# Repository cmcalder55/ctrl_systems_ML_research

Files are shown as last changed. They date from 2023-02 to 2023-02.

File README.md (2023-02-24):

# &nbsp;&nbsp;&nbsp;&nbsp;&nbsp;&nbsp;&nbsp;&nbsp;&nbsp;&nbsp;&nbsp;&nbsp;&nbsp;&nbsp;&nbsp;&nbsp;&nbsp;&nbsp;&nbsp;Automation and Machine Learning for Robust   &nbsp;&nbsp;&nbsp;&nbsp;&nbsp;&nbsp;&nbsp;&nbsp;&nbsp;&nbsp;&nbsp;&nbsp;&nbsp;&nbsp;&nbsp;&nbsp;&nbsp;&nbsp;&nbsp;&nbsp;&nbsp;&nbsp;&nbsp;&nbsp;&nbsp;&nbsp;Self-Tuning of Magneto-Optical Traps

## Abstract  
In recent years the Magneto-Optical Trap (MOT) has become a standard technology used in almost every AMO laboratory (Atomic, Molecular, and Optical Physics). While technology of individual components has improved over time, the alignment of the trap still requires tedious maintenance performed hands-on by skilled experimentalists. The project focuses on developing a custom control system for piezoelectric mirror mounts responsible for the position adjustment of the lasers beams in the experimental setup. The implementation consists of LabVIEW interface and python algorithms, supported by rotary encoders to correct for hysteresis of the devices. The control system’s efficiency is tested through fiber coupling, typically performed manually, with the overall goal of full automation. This contributes to the group’s goal of automating the MOT as a whole, thereby saving time and making experimental results more repeatable. 

The feedback from the LabVIEW controllers is used in the Python program to determine the position of the center of the fiber cable and aim the laser. After successful coupling, machine learning models are used to evaluate the outputs of the entire experiment and determine the optimal experimental inputs. These models also help reveal any correlations between the mirror position, laser and fiber coupling, the rate of successful cloud creation, and the characterisitics of any resulting atom clouds. By implementing these controllers and evaluation systems, the overall goal is to fully automate this process and the experiment as a whole.

<p align="center">
Atom cloud experimental output

<p align = "center">
Fig.1 - MOT atom cloud.
</p>

## Introduction  
Magneto-optical traps (MOTs) use lasers and magnetic fields to cool and slow down atoms. Atoms are cooled down to temperatures as low as ~15 uK, which is almost absolute zero. Atoms are fed into the experiment where they collide with lasers on the x,y, and z axes. The photons in the laser collide with the atoms and cancel out some of their momentum and push them towards the laser source. This causes friction on the atoms, slowing them further with the Doppler cooling effect. Magnetic fields in a vaccuum chamber are used to pull cooled atoms towards the center and create a "trap". Atoms in the experiment are run through the phases of this trap system multiple times, with the goal of creating a cloud of atoms that is as dense and as cold as possible.

<p align="center">

&nbsp;&nbsp;&nbsp;&nbsp;&nbsp;&nbsp;&nbsp;&nbsp;&nbsp;&nbsp;&nbsp;&nbsp;

</p>

<p align = "left">
&nbsp;&nbsp;&nbsp;&nbsp;&nbsp;&nbsp;&nbsp;&nbsp;&nbsp;&nbsp;&nbsp;&nbsp;&nbsp;&nbsp;&nbsp;&nbsp;&nbsp;&nbsp;&nbsp;&nbsp;&nbsp;&nbsp;&nbsp;&nbsp;&nbsp;&nbsp;&nbsp;&nbsp;&nbsp;&nbsp;&nbsp;&nbsp;&nbsp;&nbsp;&nbsp;&nbsp;&nbsp;Fig.2 - Slowing of atoms with photons.&nbsp;&nbsp;&nbsp;&nbsp;&nbsp;&nbsp;&nbsp;&nbsp;&nbsp;&nbsp;&nbsp;&nbsp;&nbsp;&nbsp;&nbsp;&nbsp;&nbsp;&nbsp;&nbsp;&nbsp;&nbsp;&nbsp;Fig.3 - MOT basic experimental setup.
</p>
  
Slowing down the atoms makes it significantly easier to study the atom's quantum characteristics. For example, if you are trying to read the license plate on a car, the slower the car the easier it is to read. The same concept applies to quantum properties of atoms. There are many parameters that must be controlled to run this experiment, typically requiring multiple skilled experimentalists and a huge time investment just to set up. It is very sensitive to environmental variables like ambient temperature and light, making it difficult to maintain experimental conditions. Very small changes such as microscropic drift over time in parts of the experimental setup can be the difference between a successful run and no atom cloud output at all.  

## Motivation
The overall objective of this project was to use automation approaches and optimization and machine learning techniques to remove the need for a trained operator to tune the MOT. Tuning by a human operator is extremely time consuming, and can take anywhere from six hours to days, with no guarantee of a successful experimental output. The experimental set-up is also very crowded and difficult to adjust by hand, and uses high-powered lasers that pose a safety risk while making hand adjustments. By automating these mirror mount adjustments and making them remotely controllable, the experiment will become easier to repeat and safer for experimentalists to run. Significantly reducing the set-up time also allows more runs to be done in the same time frame, allowing the group to identify the factors needed to consistently generate an atom cloud.   
  
**The individual goals were to:**  
  * Find appropriate transducers to get the relative position of the mirror mount adjusters  
  * Design and build a mechanism to attach the transducers to the mounts  
  * Make a LabVIEW program to:  
    * Remotely control the mount adjusters   
    * Determine their absolute position using the transducers  
  * Make the control system closed loop to compensate for hysteresis  
  * Write a Python program to run the LabVIEW program and optimize mirror adjustments  
  * Use machine learning libraries in Python to analyze experimental outputs and explore coupling profiles  

### Commercial Solutions
A huge limitation to solving this problem to automatic mount adjustment is the high level of precision required and lack of space in the set-up to add transducers. When working on an atomic level, an adjustment of a few micrometers can completely misalign a mirror. Stepper motors, for example, can be controlled remotely and make fine adjustments, but they are too large and unstable to use.   
The mirror mounts on the experiment also function using a piezoelectric material, so they have a high hysteresis rate and have no built-in compensation system. Inertial actuators can be added to help have a more consistent step-size during adjustment, but they still have an open-loop design with up to 20% error between steps. The inertial actuators also limit the range of the adjuster screws while doubling their profile length, making them unusable.

<p align="center">

&nbsp;&nbsp;&nbsp;&nbsp;&nbsp;&nbsp;&nbsp;&nbsp;&nbsp;

<p align = "center">
Fig.4 - Stepper motor actuators. &nbsp;&nbsp;&nbsp;&nbsp;&nbsp;&nbsp;&nbsp;&nbsp;&nbsp;&nbsp;&nbsp;&nbsp;&nbsp;&nbsp;&nbsp;&nbsp;&nbsp;&nbsp;Fig.5 - Inertial actuators.
</p>

### Repeatability Trade-Off
The piezoelectric mirror mounts come with a controller that can be operated remotely, but the controls are not customizable to the level needed for this experiment, and the screw distance travelled is not repeatable. However, it is possible to make very fine adjustments manually due to the piezoelectric effect. This also has the advantage of being self-locking while at rest or while no power is applied, but the adjustments made to get to a position are not repeatable. This is due to a variety of reasons such as variation between mount components, variable friction when turning the screw forwards or backwards, and high hysteresis when making steps of the same size. 

<p align="center">

<p align = "center">
Fig.5 - Example of difference between forward and reverse step sizes of same input magnitude.
</p>

## Methods  
[Detailed descriptions of every component in the system and their function can be found **HERE**.](https://github.com/cmcalder55/ctrl_systems_ML_research/blob/main/LV_code_and_guide/Mount_Control_VI_Guide_2.pdf)

To compensate for this error, small rotary encoders were inserted into the adjuster screws and attached to the mount using existing screw holes. The 360 degree turn of the screw is proportional to the 0-5 V. output of the rotary encoder, giving the relative position of the screw. This information can then be used to create a feedback system using a custom P.I. controller to automatically correct positional error, as well as define and map the global screw position to utilize the full range of adjustments.   

This design is better than the commerical alternatives because the transducers have a small profile and highly accurate. The wiring system is simple (power, groud, output) and outputs an analog voltage signal, making it easy to read into LabVIEW and make an effective automated controller. This solution is also not exclusive to the mounts used in this experiment, and could be added to a wide range of products that have high hysteresis.  

Position commands are input into Python, which are then fed into LabVIEW using a TCP connection. The LabVIEW controller communicates with the native mount controller to move the screws and scale the step size to reach the desired point. A homing mode was also added to set the global origin of the adjuster screws and define the full range of the screw. The absolute position is stored to an external file, so it does not need to be re-callibrated. This is important because the controller still tries to move the screw even if it cannot be turned anymore. This can cause damage to the equipment, so it is necessary to know when a screw is approaching the end of its range. The homing system is summarized in Fig. 6 below.  

<p align="center">

<p align = "center">
Fig.6 - Homing mode control system diagram.
</p>

To move the mirrors the following steps are taken:  
* User inputs desired position
* Average transducer voltage is converted to degrees
* PI controller scales n steps based on direction (P) and degree difference (I)
* Adjuster screw is moved 20% of n steps and degree error is checked
* Continues until error is within desired range of user input
  * If within range, set steps needed to 0

<p align="center">

<p align = "center">
Fig.7 - Move mode P.I. controller feedback system diagram.
</p>

The overall system setup is shown in Fig. 8 below. Detailed descriptions of every component in the system can be found **HERE**. The steps taken can be summarized as follows:  
**1. Top level TCP communication: The “TCP_connection” VI is used to send position data from Python file “TCP_bare” to the mount 
controls subVI. The subVI outputs laser coupling percentage and the value is sent back to Python.**  
  * Read data from Python
  * Send data to subVI
  * Return data from subVI and exit
**2. Mount control subVI: The “mount_controls.vi” subVI receives an array of positions and mode number as inputs. Outputs laser 
coupling percentage.**  
  * Initialize message queue and scan for controller device, return array of controller channels
  * Create array of analog input channels and voltage sampling task
  * Separate channel for reading photodiode to check coupling percentage
  * Cluster mount channels and pairs
  * Determine mode input
    * 1 or 2 = "RUN"
    * 3 = "HOME"
    * 0/default = "END"
 **3. Execute current active mode based on dequeued message**
  * Run --> Read current laser coupling --> queue Move message
  * Move --> make adjustment --> check actual position --> re-adjust until within margin of error --> End
  * End --> store position data --> close queues --> output absolute position  
 
 The photodiode is continuously read during this process to check for any laser coupling by averaging every 100 samples.  
 
 **4. (Optional) Home: home channels and reset stored origin.**
  * Take a step in the reverse direction
  * Keep taking steps and scale by the rate of positional change
  * When the rate of change is sufficiently small, take very small and quick steps
  * Keep taking very small steps until the sensor is no longer moving (end of range of motion)
  * Store home position

<p align="center">

<p align = "center">
Fig.8 - Full system diagram.
</p>

## Results  
Using this custom controller, a user chosen position was repeatable with a high level of accuracy. It was determined that on average, the screw adjustments were 3 times as fast in the forward direction. This indicates that the friction used to move the screws using voltage control with the piezoelectric material had a significant effect on the step size. This effect means that adding a feedback system is the minimum needed to use these mounts with any degree of repeatability.  
  
Another advantage of the system created in this project is an adjustable error margin, allowing for extremely precise movements. After achieving this, the program was used to automate laser coupling with a fiber optic cable. The Python inputs were then switched from user control to inputs chosen by an optimizer made in Python. This was a goos test of accuracy, since this set-up is more sensitive than the MOT itself. After coupling was achieved, a machine learning model was used to discern the effect of coupling on the output of the MOT.

<p align="center">

&nbsp;&nbsp;&nbsp;&nbsp;&nbsp;&nbsp;&nbsp;&nbsp;&nbsp;&nbsp;&nbsp;&nbsp;&nbsp;&nbsp;&nbsp;&nbsp;&nbsp;&nbsp;

<p align = "center">
Fig.9 - Laser coupling testing and automated adjustment system diagram. &nbsp;&nbsp;&nbsp;&nbsp;&nbsp;&nbsp;&nbsp;&nbsp;&nbsp;&nbsp;&nbsp;&nbsp;&nbsp;&nbsp;&nbsp;&nbsp;&nbsp;&nbsp;&nbsp;&nbsp;&nbsp;&nbsp;&nbsp;Fig.10 - Laser coupling experimental setup.
</p>

## Discussion
Dur to time constraints, the machine learning model was not able to make any significant conclusions from the data. However, achieving automated coupling at any level was a significant step towards automating the MOT and reducing set-up time while prioritizing worker safety. If this project were to be continued, the next steps would focus on training the M.L. model with more data and fine-tuning the automated laser coupling set-up on the actual experiment.

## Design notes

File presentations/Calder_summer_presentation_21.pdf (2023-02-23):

## Automation and Machine Learning for Robust

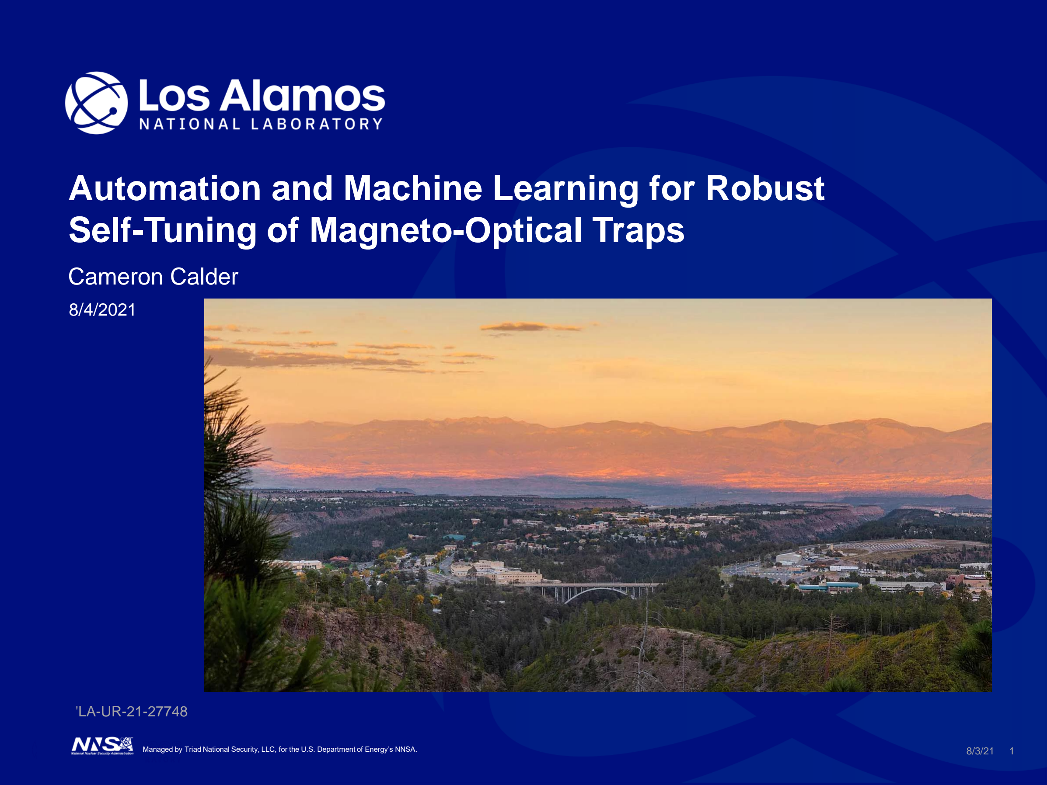
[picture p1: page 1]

Managed by Triad National Security, LLC, for the U.S. Department of Energy’s NNSA. | 8/3/21 | 1

## Self-Tuning of Magneto-Optical Traps

Cameron Calder

8/4/2021

'LA-UR-21-27748

## Motivation

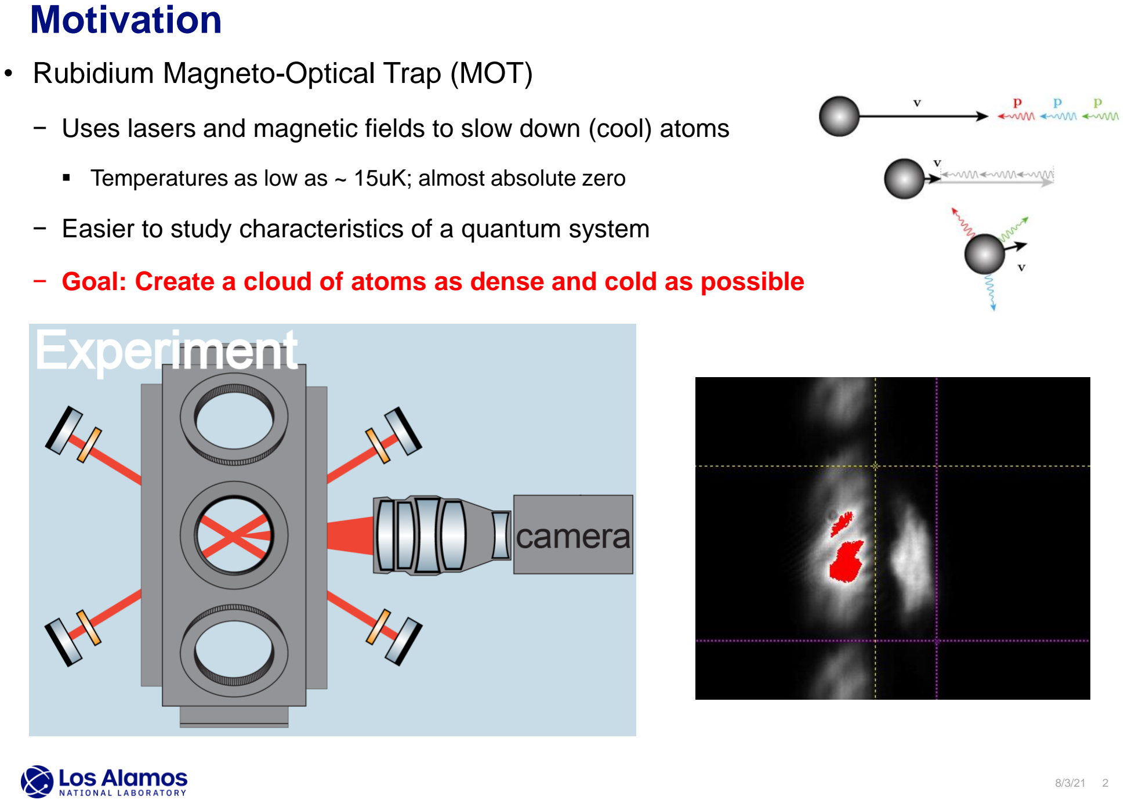
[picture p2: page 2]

8/3/21 2

- Rubidium Magneto-Optical Trap (MOT)

− Uses lasers and magnetic fields to slow down (cool) atoms

- Temperatures as low as ~ 15uK; almost absolute zero

− Easier to study characteristics of a quantum system

− Goal: Create a cloud of atoms as dense and cold as possible

## Experimental Set-Up

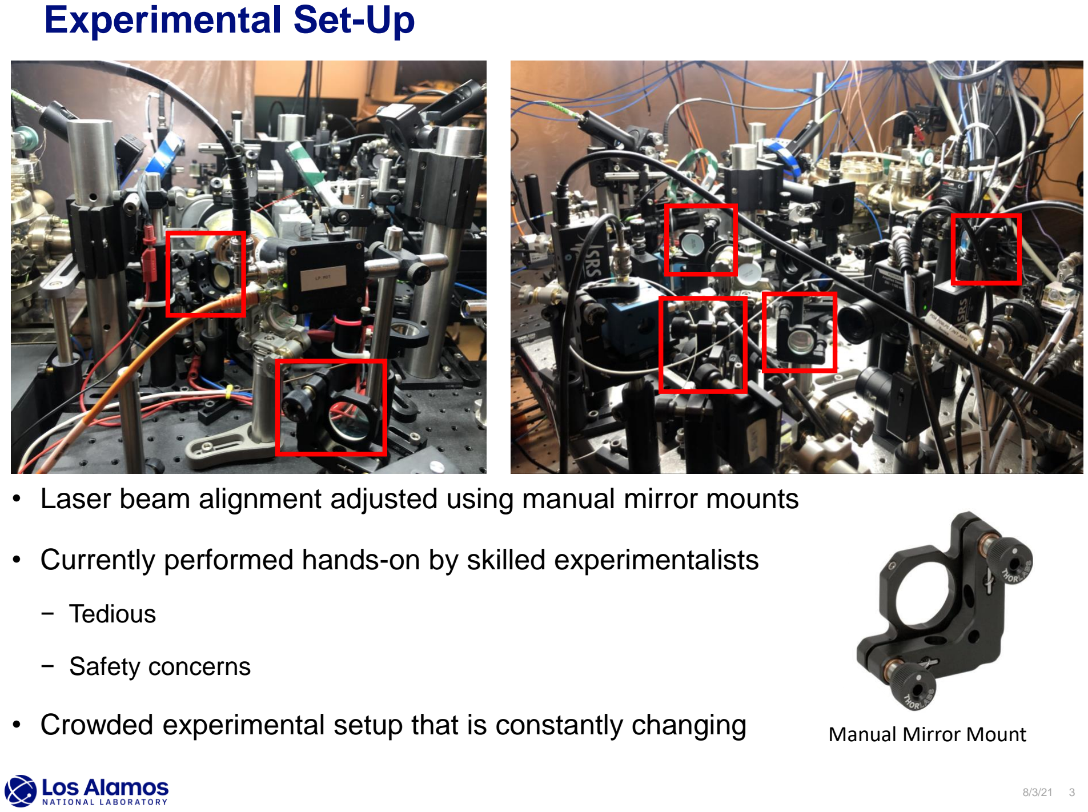
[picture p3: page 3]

- Laser beam alignment adjusted using manual mirror mounts
- Currently performed hands-on by skilled experimentalists

− Tedious

− Safety concerns

- Crowded experimental setup that is constantly changing | Manual Mirror Mount

## Commercial Solutions and Limitations

- Current mounts allow fine adjustment, but can only be moved manually

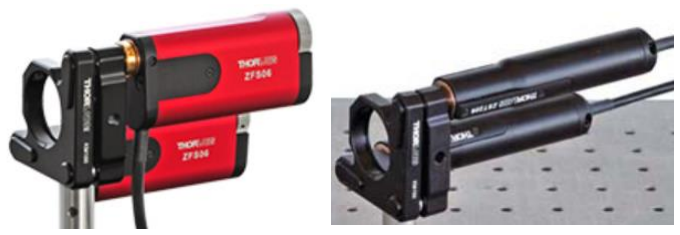
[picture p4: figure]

4:1 Length | 5:1 Length

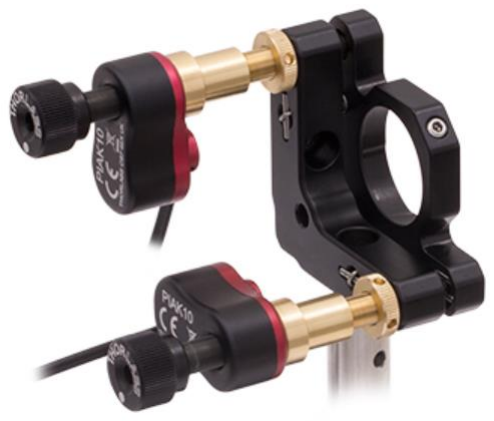
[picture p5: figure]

2:1 Length

- Piezoelectric Inertial Actuator ‒ Cannot move full screw range ‒ Still requires external feedback
- Stepper Motors
‒ Too large
‒ Unstable

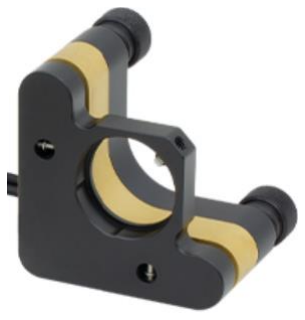
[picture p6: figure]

Piezoelectric Mirror Mount

Manufacturer Solutions

- Piezoelectric mounts can be moved remotely, but screw
distance traveled not repeatable − Fine adjustment
− Similar size

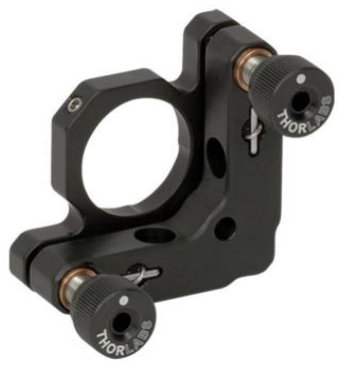
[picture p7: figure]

Manual Mirror Mount

## What is a Piezoelectric Mount?

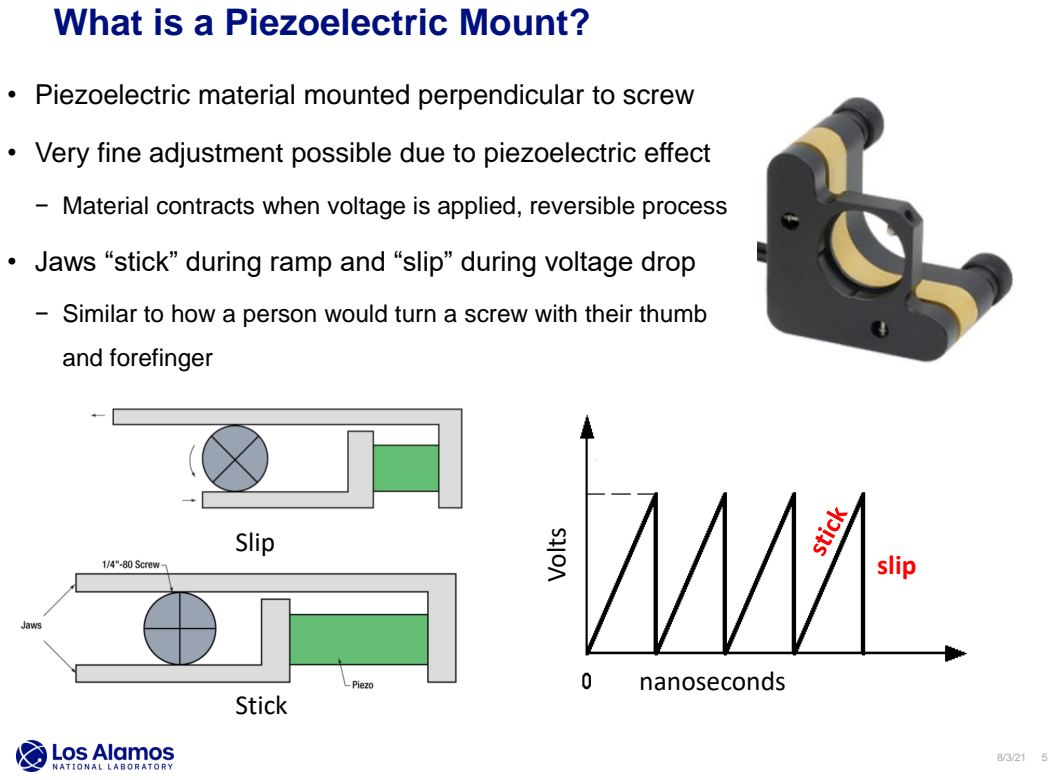
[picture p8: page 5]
and forefinger; slip; nanoseconds; Volts; Slip; Stick

• Piezoelectric material mounted perpendicular to screw

• Very fine adjustment possible due to piezoelectric effect

− Material contracts when voltage is applied, reversible process

• Jaws “stick” during ramp and “slip” during voltage drop

− Similar to how a person would turn a screw with their thumb

## Repeatability Trade-Off

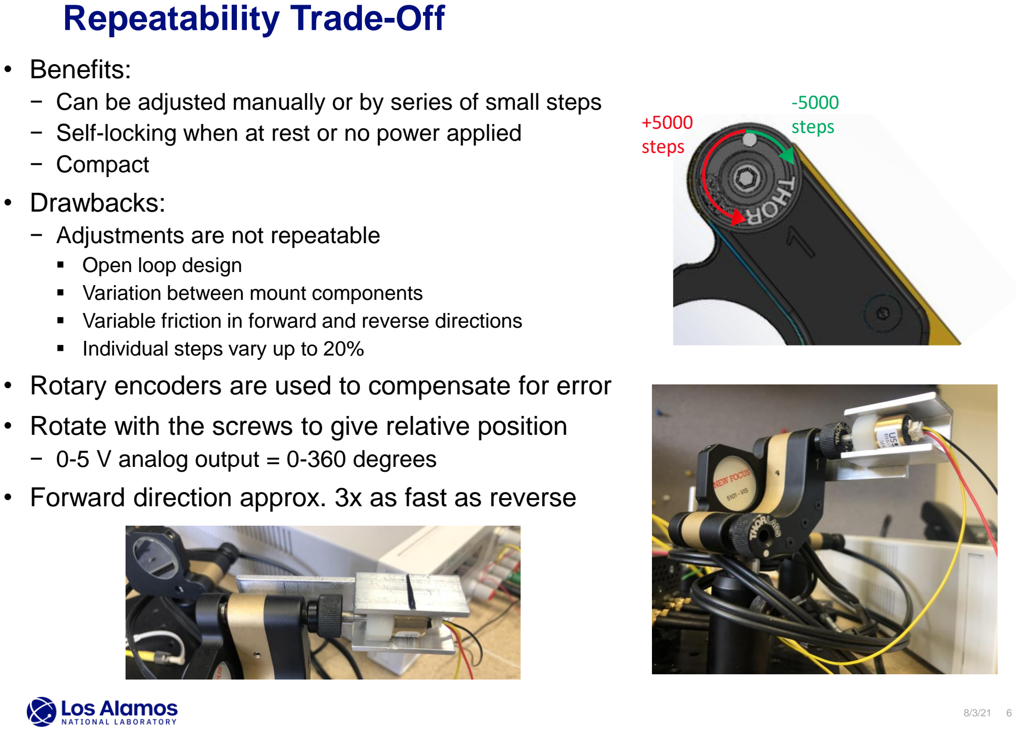
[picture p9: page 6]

+5000
steps

-5000
steps
- Benefits:
− Can be adjusted manually or by series of small steps − Self-locking when at rest or no power applied
− Compact
- Drawbacks:
− Adjustments are not repeatable
- Open loop design
- Variation between mount components
- Variable friction in forward and reverse directions
- Individual steps vary up to 20%
- Rotary encoders are used to compensate for error
- Rotate with the screws to give relative position
− 0-5 V analog output = 0-360 degrees
- Forward direction approx. 3x as fast as reverse

## Why Our Design is Better

- Transducers are small and accurate − 1 step = 0.02 degrees
− 70% the length of the mount
- Easy wiring and analog output
− 3 wires- power, ground, output
− Read using DAQ directly into LabVIEW
- Simple to attach and reproduce
− One Al bracket (1)
− One Al U-channel (2)
− One nylon hex nut (3)
− One plastic spacer (4)
− Two flathead screws (5)
− One mounting screw (6)
- Comparable price
− Solution not exclusive to these mounts

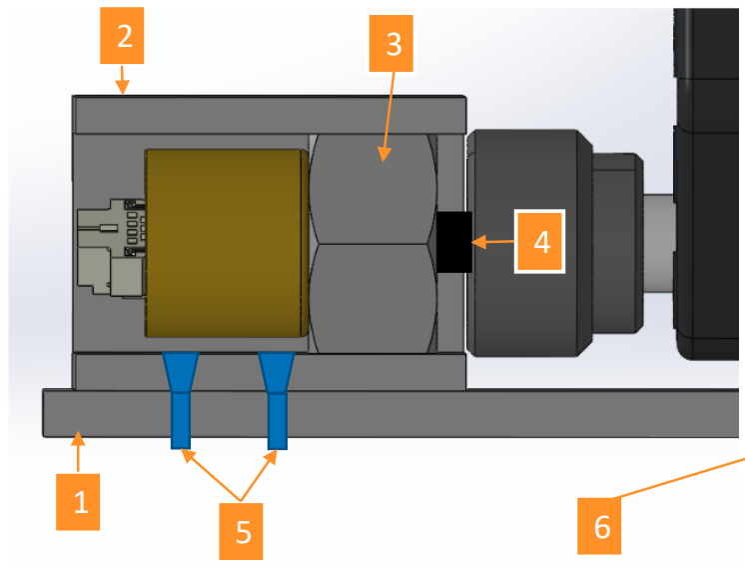
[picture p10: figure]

Solution | Parts Cost ($) | Mount Cost ($) | Total Cost ($)
Rotary Encoder | 130 | 1200 | 1330
Stepper Motor 1 | 2200 | 40 | 2240
Stepper Motor 2 | 1300 | 40 | 1340

## Overall Adjuster Screw Control System

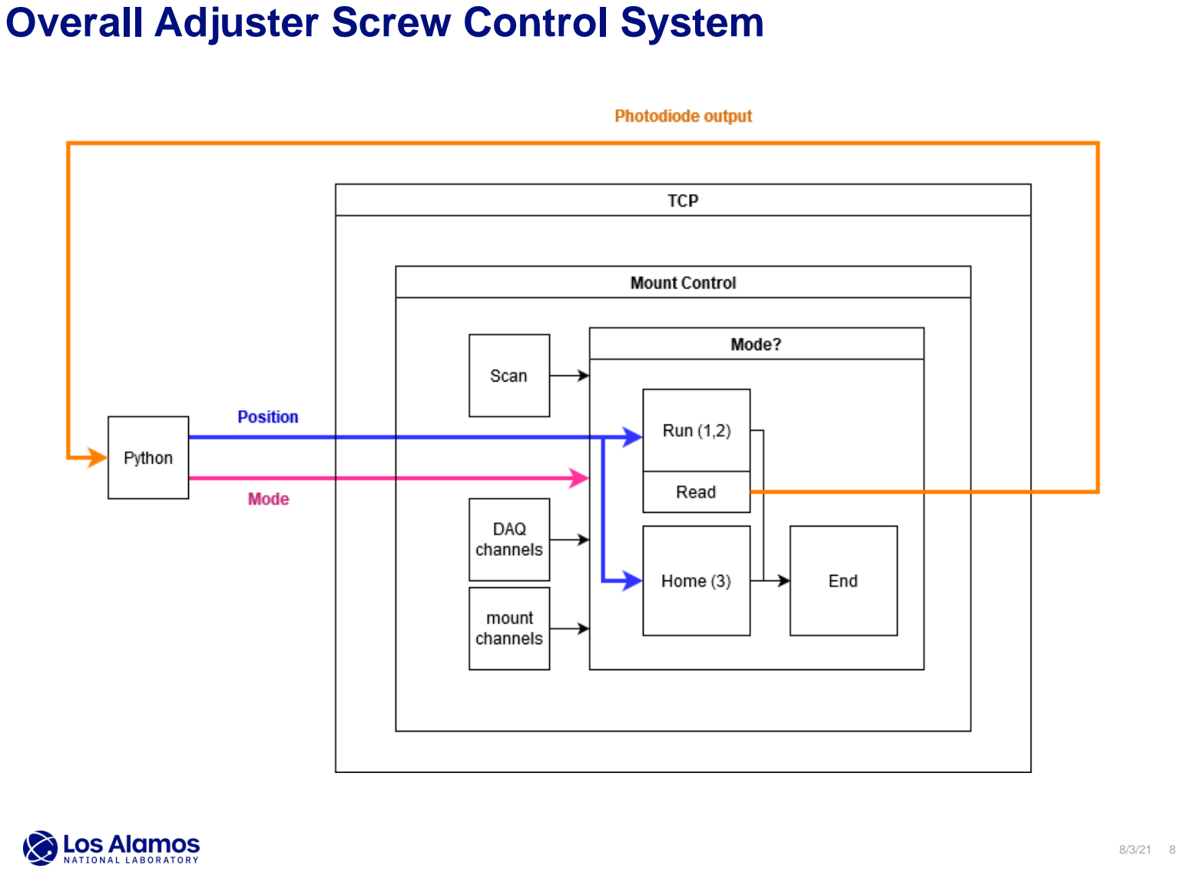
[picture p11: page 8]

## Finding Home

- Transducer only has range of 0-360 degrees
− One rotation
- Overall screw range is 12.7 full rotations
- How can we control the screw over the entire range?

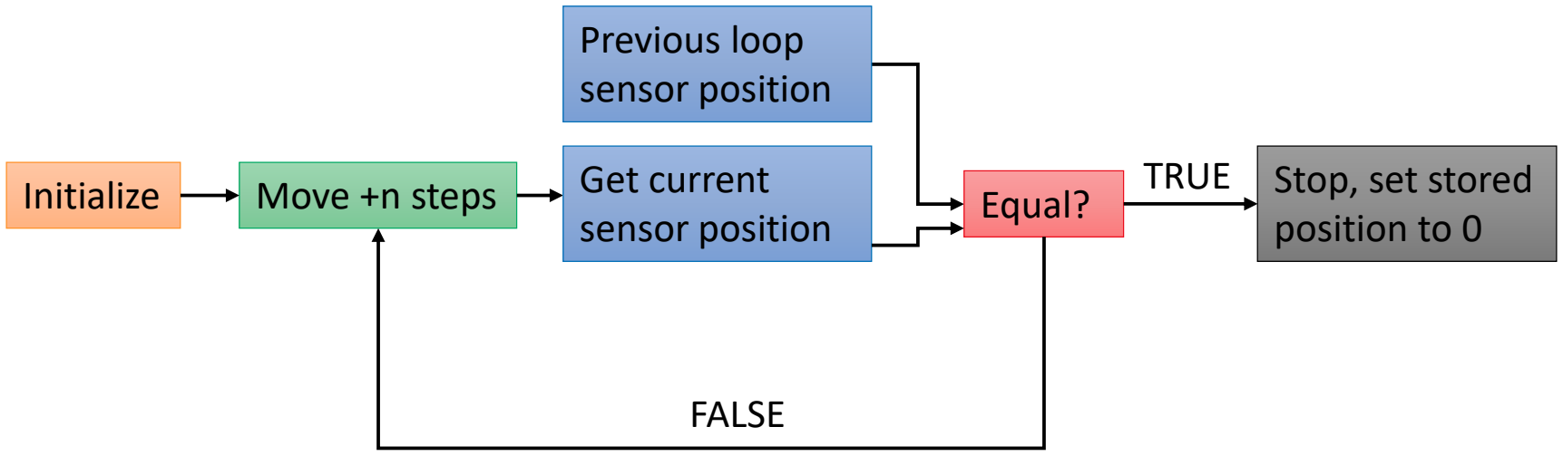
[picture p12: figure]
Initialize; Move +n steps; Get current; sensor position; Previous loop sensor position; FALSE; Equal?; Stop, set stored; position to 0; TRUE

- Only have to initialize on first run
- Absolute position stored to file after screw adjustment based on step change from 0
- Step position / 360 = rotation position

## Using Feedback for Accurate Adjustment

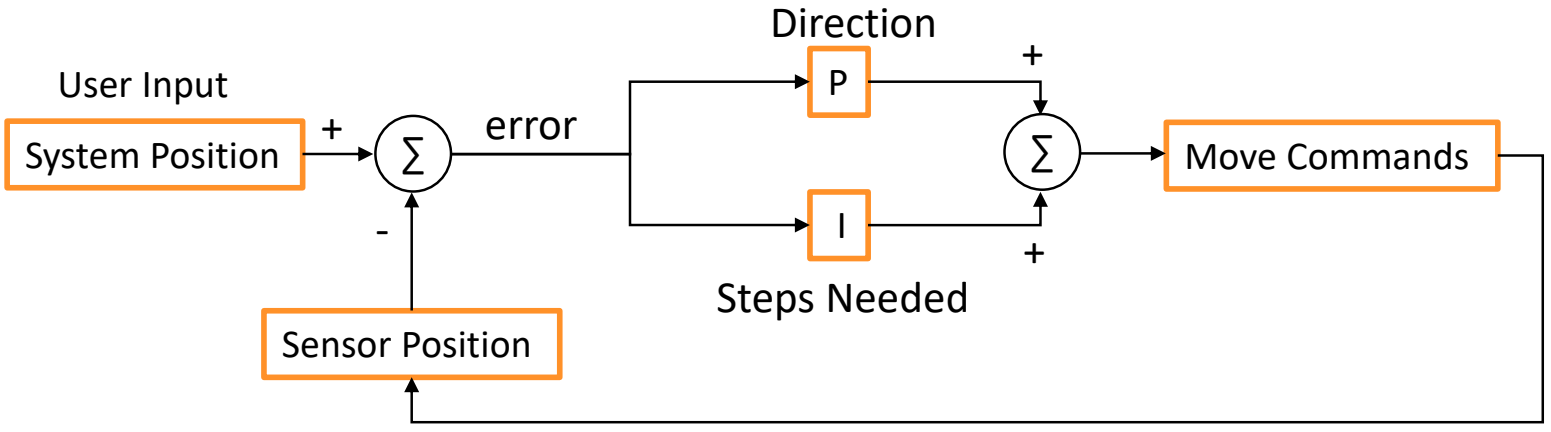
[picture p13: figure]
Sensor Position; System Position; User Input; Move Commands; error; Direction; Steps Needed

- User inputs desired position
- Average transducer voltage is converted to degrees
- PI controller scales n steps based on direction (P) and degree difference (I)
- Adjuster screw is moved 20% of n steps and degree error is checked
- Continues until error is within desired range of user input
− If within range, set steps needed to 0

## System Response

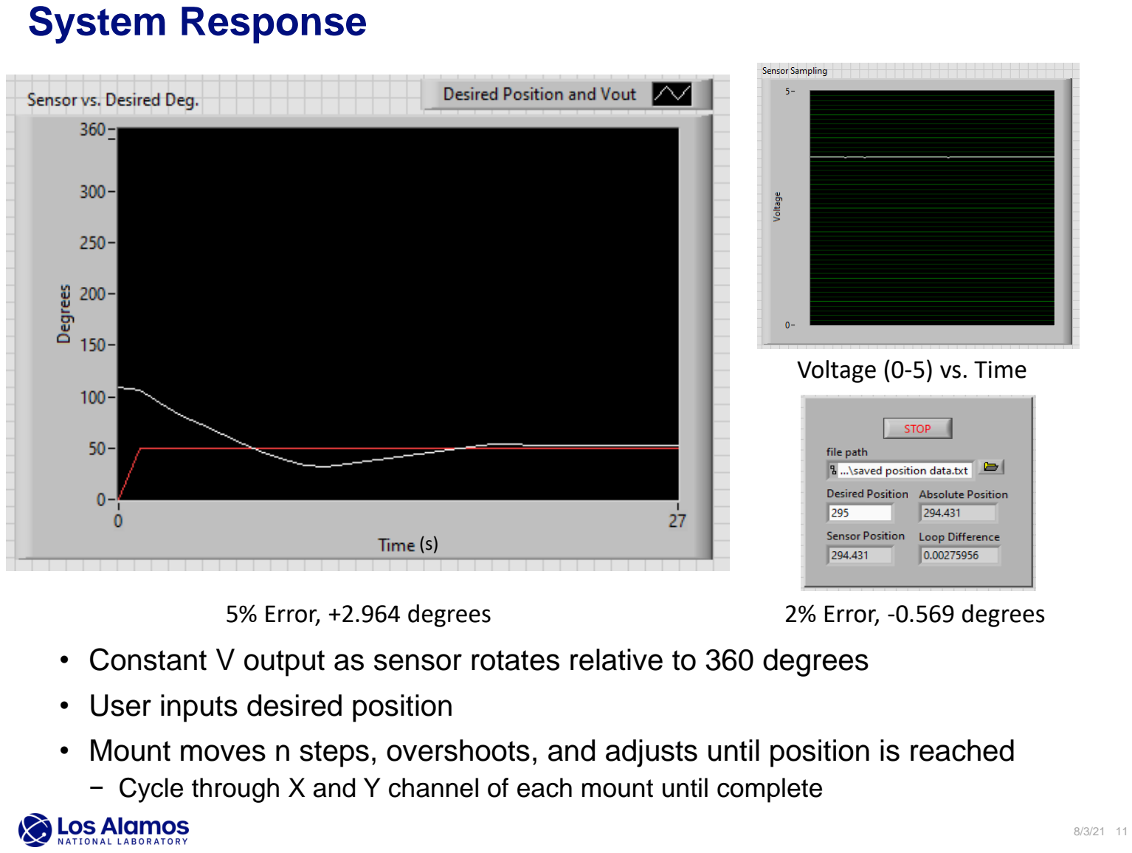
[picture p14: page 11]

- Constant V output as sensor rotates relative to 360 degrees
- User inputs desired position
- Mount moves n steps, overshoots, and adjusts until position is reached − Cycle through X and Y channel of each mount until complete
5% Error, +2.964 degrees | 2% Error, -0.569 degrees
(s) | Voltage (0-5) vs. Time

## Testing and Optimization

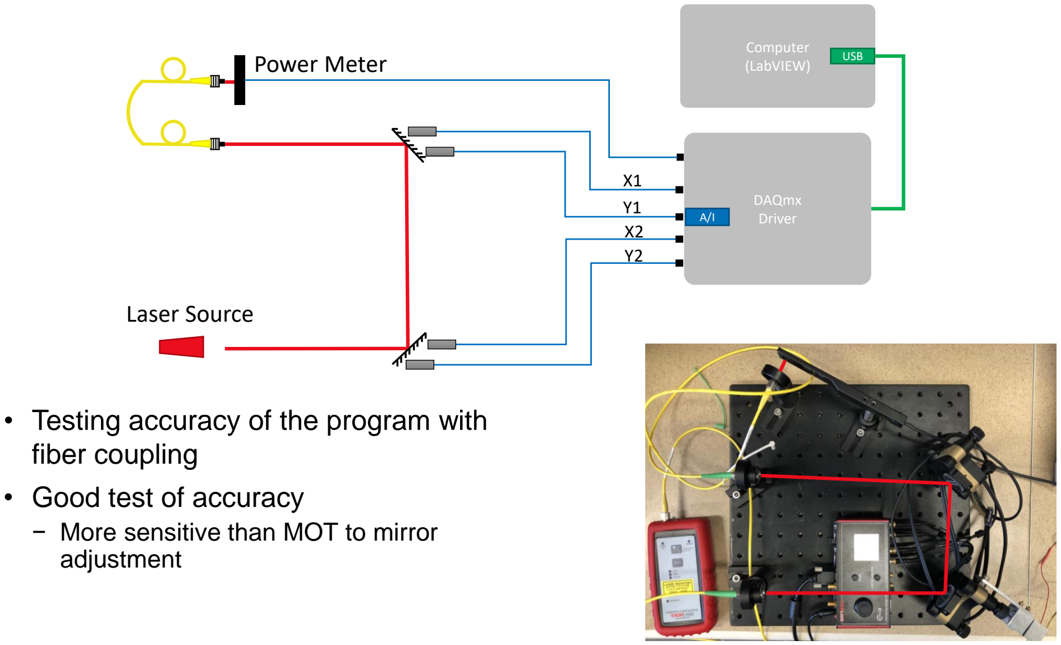
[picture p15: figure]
DAQmx Driver; • Testing accuracy of the program with fiber coupling; • Good test of accuracy; − More sensitive than MOT to mirror adjustment; Computer; (LabVIEW); USB; Laser Source; Power Meter

Summary

## Summary and Outlook

Outlook

- Found suitable transducers for screw position
- Designed simple mount assembly
- Scalable control of piezoelectric stages in LabVIEW including:
− Automatic adjusting with custom PI controller
− Homing procedure
− Output of absolute position over full screw translation range
− Storage of end position to correct unwanted changes between runs
- Assembled coupling system for testing
- Automated fiber coupling
- Continue to develop Python program for MOT self-adjustment using Python optimization and machine learning packages
− SciPy.optimize()
− Mystic, PyTorch

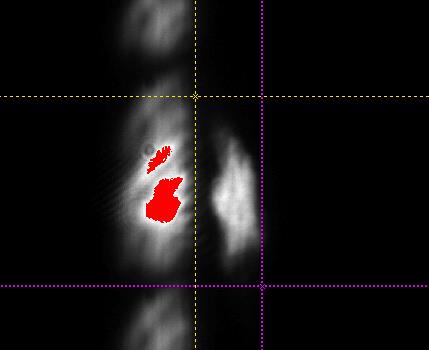
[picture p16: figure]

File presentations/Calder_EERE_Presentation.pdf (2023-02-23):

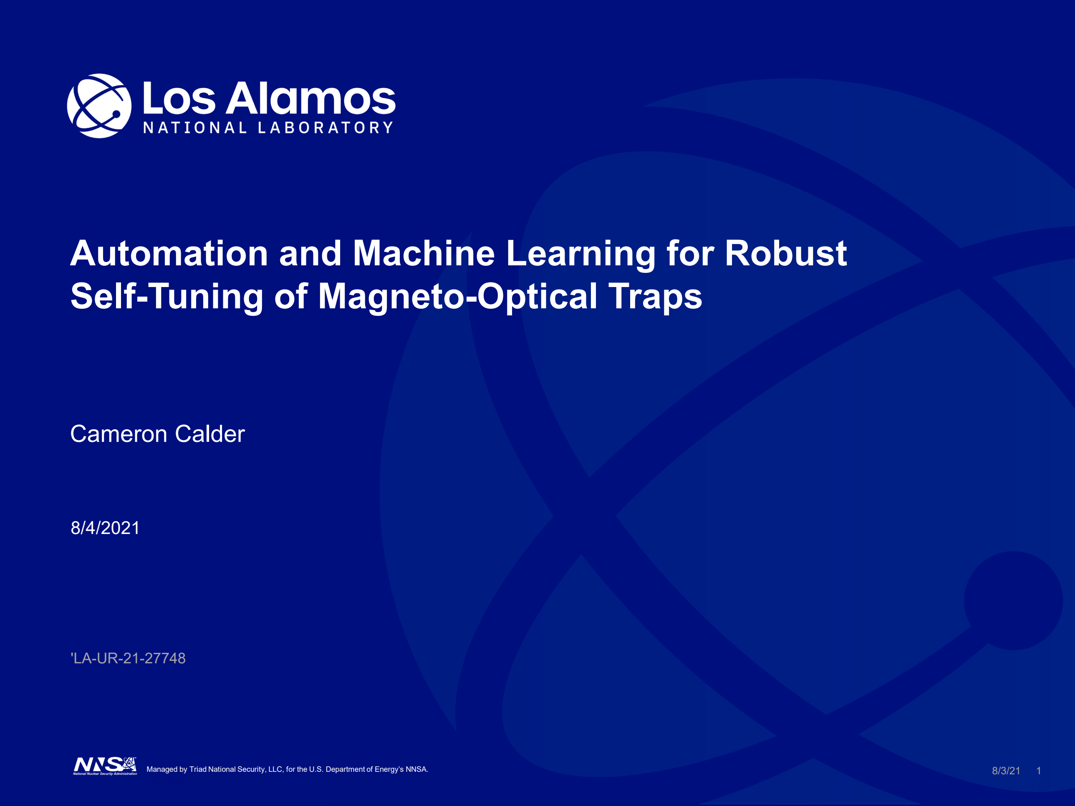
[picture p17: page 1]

Managed by Triad National Security, LLC, for the U.S. Department of Energy’s NNSA. | 8/3/21 1

## Automation and Machine Learning for Robust Self-Tuning of Magneto-Optical Traps

Cameron Calder

8/4/2021

'LA-UR-21-27748

## Motivation

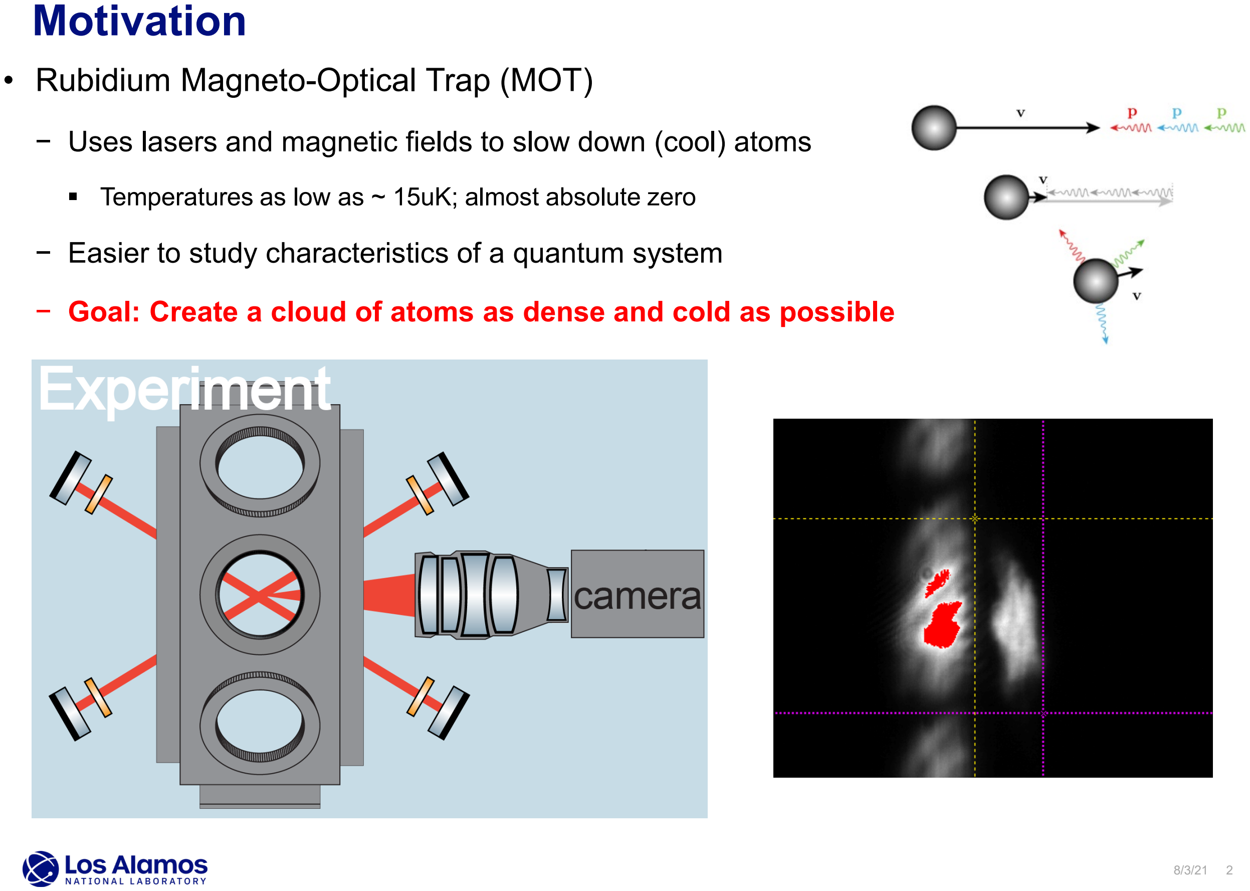
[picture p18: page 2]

8/3/21 2

- Rubidium Magneto-Optical Trap (MOT)
− Uses lasers and magnetic fields to slow down (cool) atoms
- Temperatures as low as ~ 15uK; almost absolute zero
− Easier to study characteristics of a quantum system
− Goal: Create a cloud of atoms as dense and cold as possible

## Experimental Set-Up

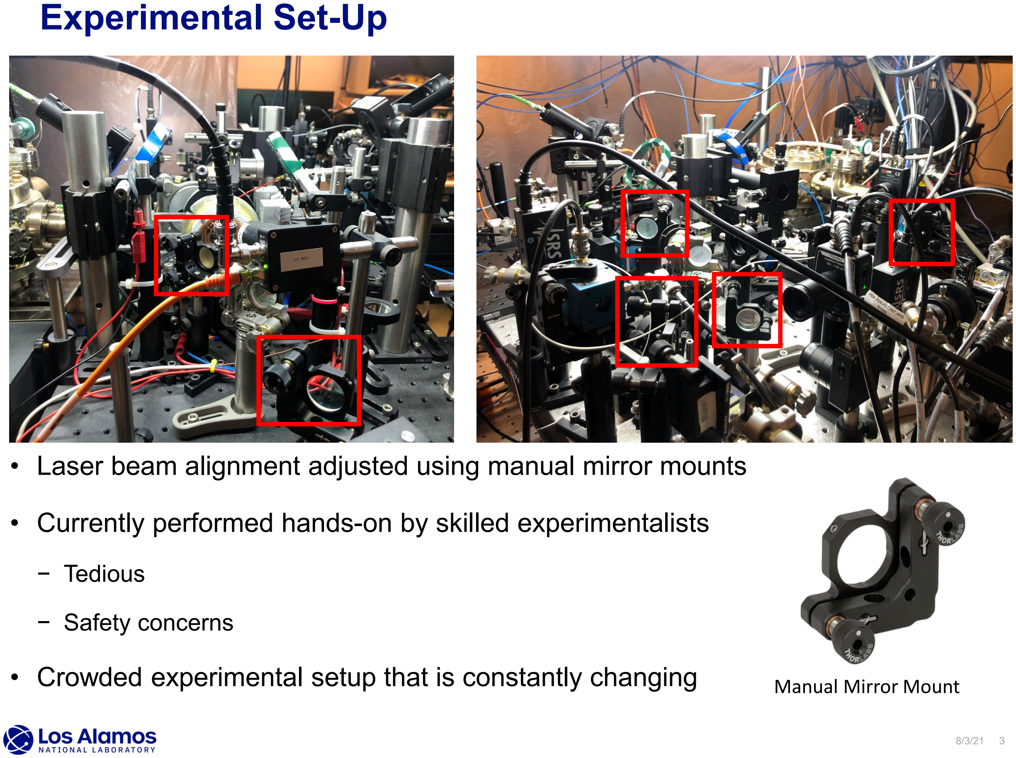
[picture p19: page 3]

- Laser beam alignment adjusted using manual mirror mounts
- Currently performed hands-on by skilled experimentalists
− Tedious
− Safety concerns
- Crowded experimental setup that is constantly changing Manual Mirror Mount

## Commercial Solutions and Limitations

- Current mounts allow fine adjustment, but can only be moved manually

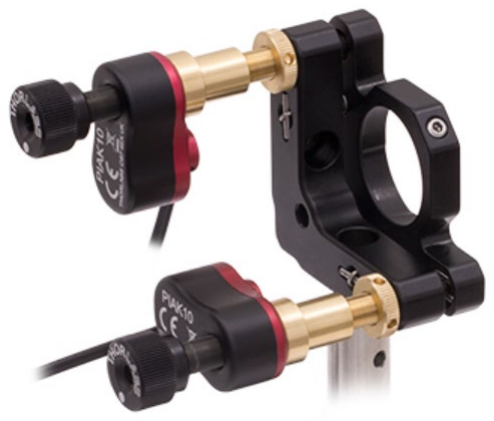
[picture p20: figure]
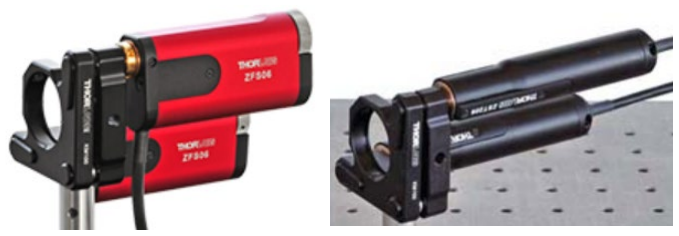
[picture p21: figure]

4:1 Length | 5:1 Length | 2:1 Length
- Piezoelectric Inertial Actuator ‒ Cannot move full screw range ‒ Still requires external feedback
- Stepper Motors
‒ Too large
‒ Unstable

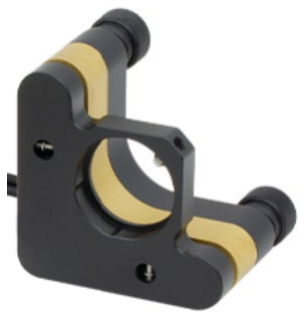
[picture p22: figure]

Piezoelectric Mirror Mount

Manufacturer Solutions

- Piezoelectric mounts can be moved remotely, but screw
distance traveled not repeatable − Fine adjustment
− Similar size

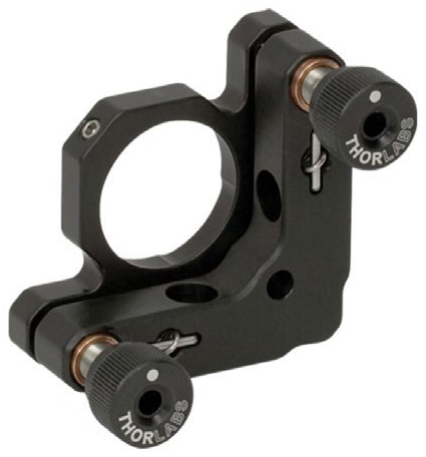
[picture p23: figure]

Manual Mirror Mount

## What is a Piezoelectric Mount?

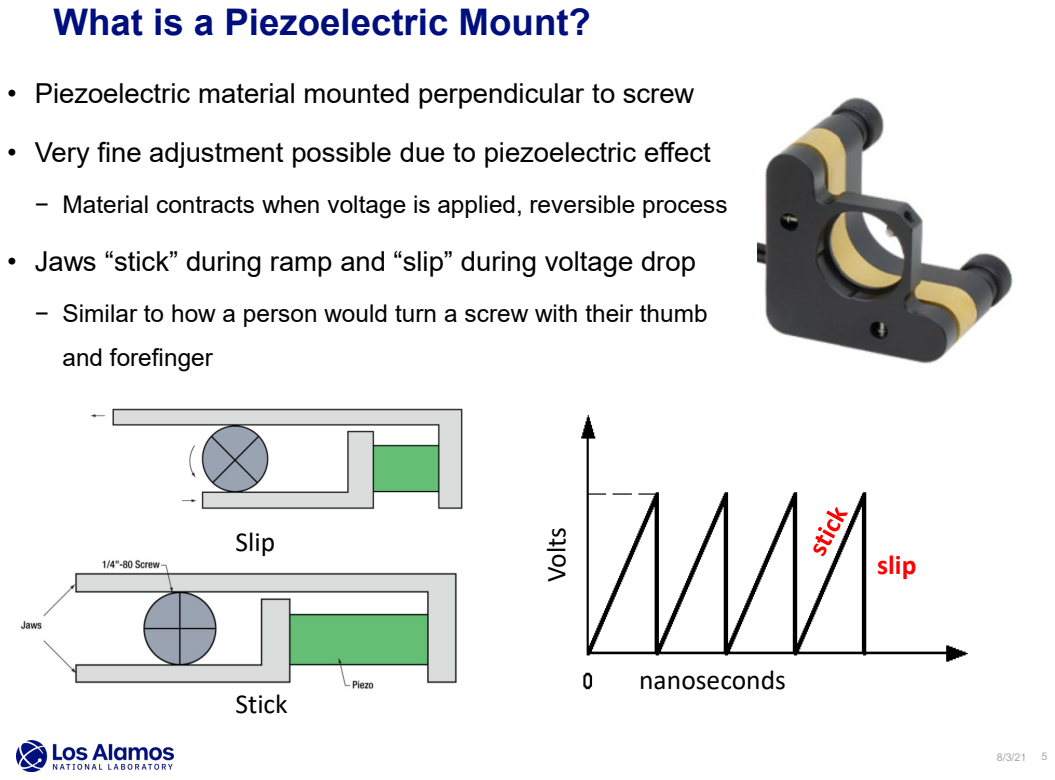
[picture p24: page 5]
slip; nanoseconds; Volts; Slip; Stick

• Piezoelectric material mounted perpendicular to screw
• Very fine adjustment possible due to piezoelectric effect
− Material contracts when voltage is applied, reversible process
• Jaws “stick” during ramp and “slip” during voltage drop
− Similar to how a person would turn a screw with their thumb
and forefinger

## Repeatability Trade-Off


+5000
steps

-5000
steps
- Benefits:
− Can be adjusted manually or by series of small steps − Self-locking when at rest or no power applied
− Compact
- Drawbacks:
− Adjustments are not repeatable
- Open loop design
- Variation between mount components
- Variable friction in forward and reverse directions
- Individual steps vary up to 20%
- Rotary encoders are used to compensate for error
- Rotate with the screws to give relative position
− 0-5 V analog output = 0-360 degrees
- Forward direction approx. 3x as fast as reverse

## Why Our Design is Better

- Transducers are small and accurate − 1 step = 0.02 degrees
− 70% the length of the mount
- Easy wiring and analog output
− 3 wires- power, ground, output
− Read using DAQ directly into LabVIEW
- Simple to attach and reproduce
− One Al bracket (1)
− One Al U-channel (2)
− One nylon hex nut (3)
− One plastic spacer (4)
− Two flathead screws (5)
− One mounting screw (6)
- Comparable price
− Solution not exclusive to these mounts


Solution | Parts Cost ($) | Mount Cost ($) | Total Cost ($)
Rotary Encoder | 130 | 1200 | 1330
Stepper Motor 1 | 2200 | 40 | 2240
Stepper Motor 2 | 1300 | 40 | 1340

## Finding Home

- Transducer only has range of 0-360 degrees
− One rotation
- Overall screw range is 12.7 full rotations
- How can we control the screw over the entire range?

Initialize; YES/NO; Move +n steps; Get current; sensor position; Previous loop sensor position; FALSE; Equal?; Stop, set stored; position to 0; TRUE

- Only have to initialize on first run
- Absolute position stored to file after screw adjustment based on step change from 0
- Step position / 360 = rotation position

## Overall Adjuster Screw Control System

Create Controller and Device; Scan SN and Device ID; Create DAQ Channels; Store position; Sample Voltage; Update Steps; Move adjuster screw; Create Message Queue; OK → Update Steps STOP → End Program; Enqueue Message; Dequeue Message; Stop?; PI Controller; Message Producer; Message Consumer; =0 →STOP; Message Case; +/- for abs. position; Read Position File

## Using Feedback for Accurate Adjustment

Sensor Position; System Position; User Input; Move Commands; error; Direction; Steps Needed

- User inputs desired position
- Average transducer voltage is converted to degrees
- PI controller scales n steps based on direction (P) and degree difference (I)
- Adjuster screw is moved 20% of n steps and degree error is checked
- Continues until error is within desired range of user input
− If within range, set steps needed to 0

## System Response


- Constant V output as sensor rotates relative to 360 degrees
- User inputs desired position
- Mount moves n steps, overshoots, and adjusts until position is reached − Cycle through X and Y channel of each mount until complete
5% Error, +2.964 degrees | 2% Error, -0.569 degrees
(s) | Voltage (0-5) vs. Time

## Testing and Optimization

DAQmx Driver; • Testing accuracy of the program with fiber coupling • Good test of accuracy − More sensitive than MOT to mirror adjustment; Computer; (LabVIEW); USB; Laser Source; Power Meter

Summary

## Summary and Outlook

Outlook
- Found suitable transducers for screw position
- Designed simple mount assembly
- Scalable control of piezoelectric stages in LabVIEW including:
− Automatic adjusting with custom PI controller
− Homing procedure
− Output of absolute position over full screw translation range
− Storage of end position to correct unwanted changes between runs
- Assembled coupling system for testing
- Automated fiber coupling
- Develop Python program for MOT self-adjustment using Python optimization and machine learning packages
− SciPy.optimize
− Mystic


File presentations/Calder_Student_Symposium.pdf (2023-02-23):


Managed by Triad National Security, LLC, for the U.S. Department of Energy’s NNSA. | 8/3/21 1

## Automation and Machine Learning for Robust Self-Tuning of Magneto-Optical Traps

Cameron Calder

8/3/2021

LA-UR-21-27580

## Motivation


8/3/21 2

- Rubidium Magneto-Optical Trap (MOT)
− Uses lasers and magnetic fields to slow down (cool) atoms
- Temperatures as low as ~ 15uK; almost absolute zero
− Easier to study characteristics of a quantum system
− Goal: Create a cloud of atoms as dense and cold as possible

## Experimental Set-Up


- Laser beam alignment adjusted using manual mirror mounts
- Currently performed hands-on by skilled experimentalists
− Tedious
− Safety concerns
- Crowded experimental setup that is constantly changing Manual Mirror Mount

## Commercial Solutions and Limitations

- Current mounts allow fine adjustment, but can only be moved manually


4:1 Length | 5:1 Length | 2:1 Length
- Piezoelectric Inertial Actuator ‒ Cannot move full screw range ‒ Still requires external feedback
- Stepper Motors
‒ Too large
‒ Unstable


Piezoelectric Mirror Mount

Manufacturer Solutions

- Piezoelectric mounts can be moved remotely, but screw
distance traveled not repeatable − Fine adjustment
− Similar size


Manual Mirror Mount

## What is a Piezoelectric Mount?

slip; nanoseconds; Volts; Slip; Stick

• Piezoelectric material mounted perpendicular to screw
• Very fine adjustment possible due to piezoelectric effect
− Material contracts when voltage is applied, reversible process
• Jaws “stick” during ramp and “slip” during voltage drop
− Similar to how a person would turn a screw with their thumb
and forefinger

## Repeatability Trade-Off


+5000
steps

-5000
steps
- Benefits:
− Can be adjusted manually or by series of small steps − Self-locking when at rest or no power applied
− Compact
- Drawbacks:
− Adjustments are not repeatable
- Open loop design
- Variation between mount components
- Variable friction in forward and reverse directions
- Individual steps vary up to 20%
- Rotary encoders are used to compensate for error
- Rotate with the screws to give relative position
− 0-5 V analog output = 0-360 degrees
- Forward direction approx. 3x as fast as reverse

## Using Feedback for Accurate Adjustment

Sensor Position; System Position; User Input; Move Commands; error

- User inputs desired position
- Average transducer voltage is converted to degrees
- PI controller scales steps based on direction (P) and position difference (I)
- Adjuster screw is moved n steps and error is checked
- Continues until error is within desired range of user input
− Change in degrees after moving summed to determine absolute position

## System Response


- Constant V output as sensor rotates relative to 360 degrees
- User inputs desired position
- Mount moves n steps, overshoots, and adjusts until position is reached
5% Error, +2.964 degrees | 2% Error, -0.569 degrees
(s) | Voltage (0-5) vs. Time

## Testing and Optimization

DAQmx Driver; • Testing accuracy of the program with fiber coupling • Good test of accuracy − More sensitive than MOT to mirror adjustment; Computer; (LabVIEW); USB; Laser Source; Power Meter

Summary

## Summary and Outlook

Outlook
- Found suitable transducers for screw position
- Designed simple mount assembly
- Scalable control of piezoelectric stages in LabVIEW including:
− Automatic adjusting with custom PI controller
− Homing procedure
− Output of absolute position over full screw translation range
− Storage of end position to correct unwanted changes between runs
- Assembled coupling system for testing
- Automated fiber coupling
- Develop Python program for MOT self-adjustment using Python optimization and machine learning packages
− SciPy.optimize
− Mystic

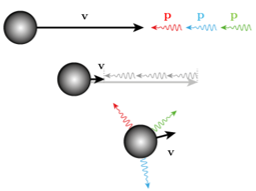
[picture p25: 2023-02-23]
readme_graphics/momentum_s1.png

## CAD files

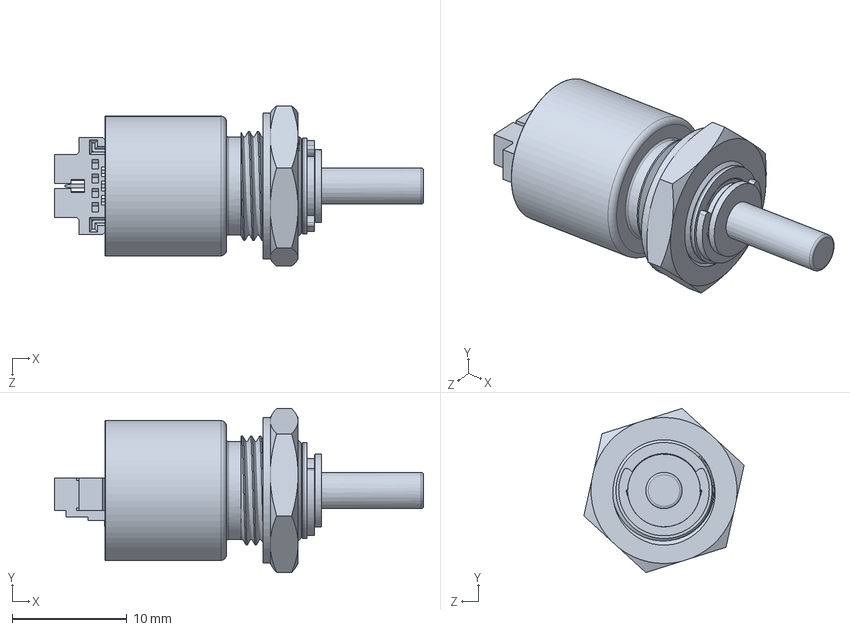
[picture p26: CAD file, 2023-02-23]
mirror_mounts_SW/MA3-X-125-D.SLDPRT
32.2 x 14.3 x 14.0 mm

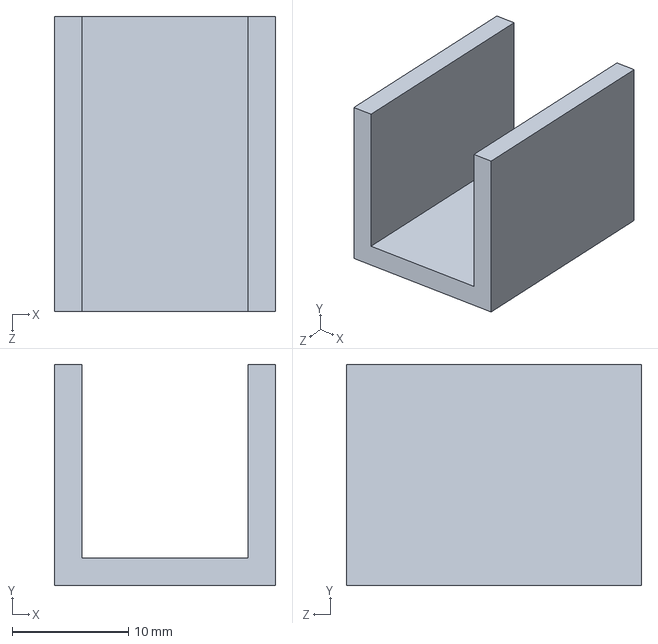
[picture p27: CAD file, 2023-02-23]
mirror_mounts_SW/9001K947_ARCHITECTURAL 6063 ALUMINUM U-CHANNEL.SLDPRT
19.1 x 19.1 x 25.4 mm

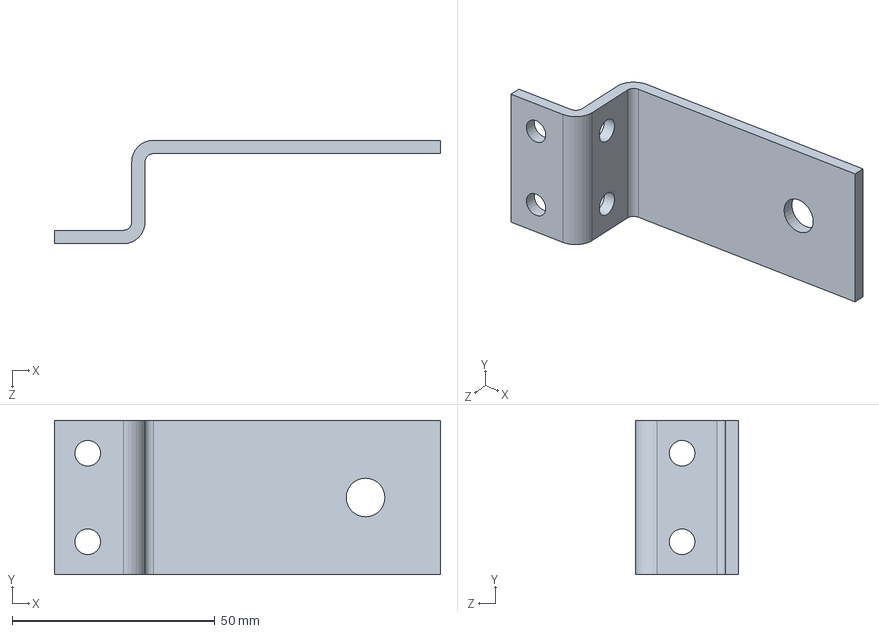
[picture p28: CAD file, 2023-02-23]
mirror_mounts_SW/1030A130_BRACKET.SLDPRT
95.2 x 38.1 x 25.5 mm

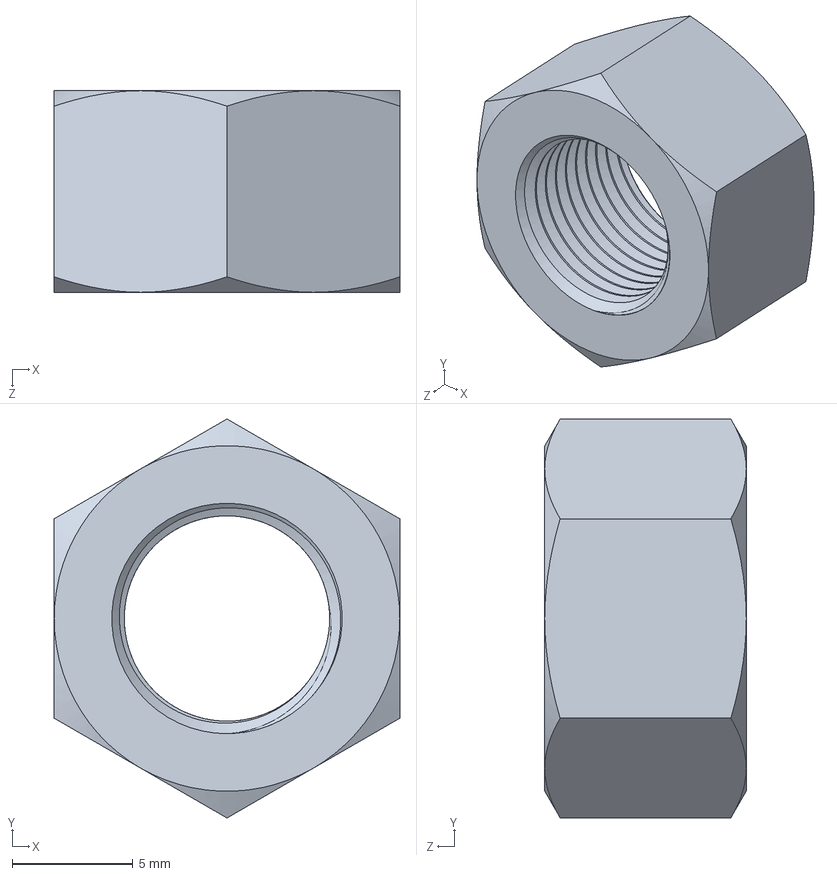
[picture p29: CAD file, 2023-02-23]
mirror_mounts_SW/90670A246_6061 ALUMINUM HEX NUT.SLDPRT
14.3 x 16.5 x 8.33 mm

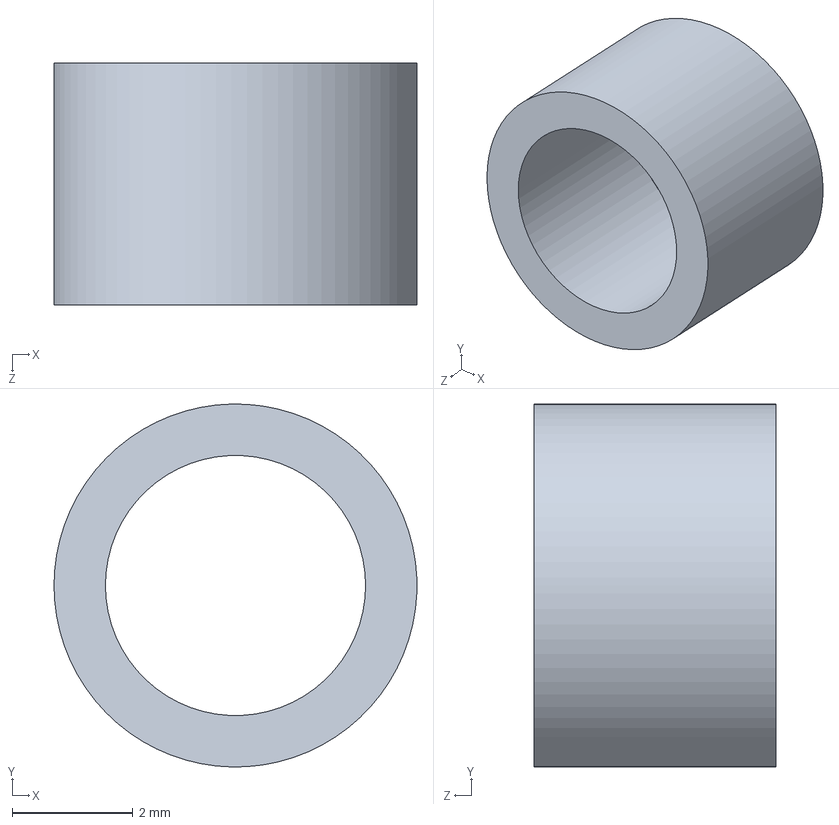
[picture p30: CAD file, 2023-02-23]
mirror_mounts_SW/99072A141_BLACK NYLON UNTHREADED SPACER.SLDPRT
6.00 x 6.00 x 4.00 mm

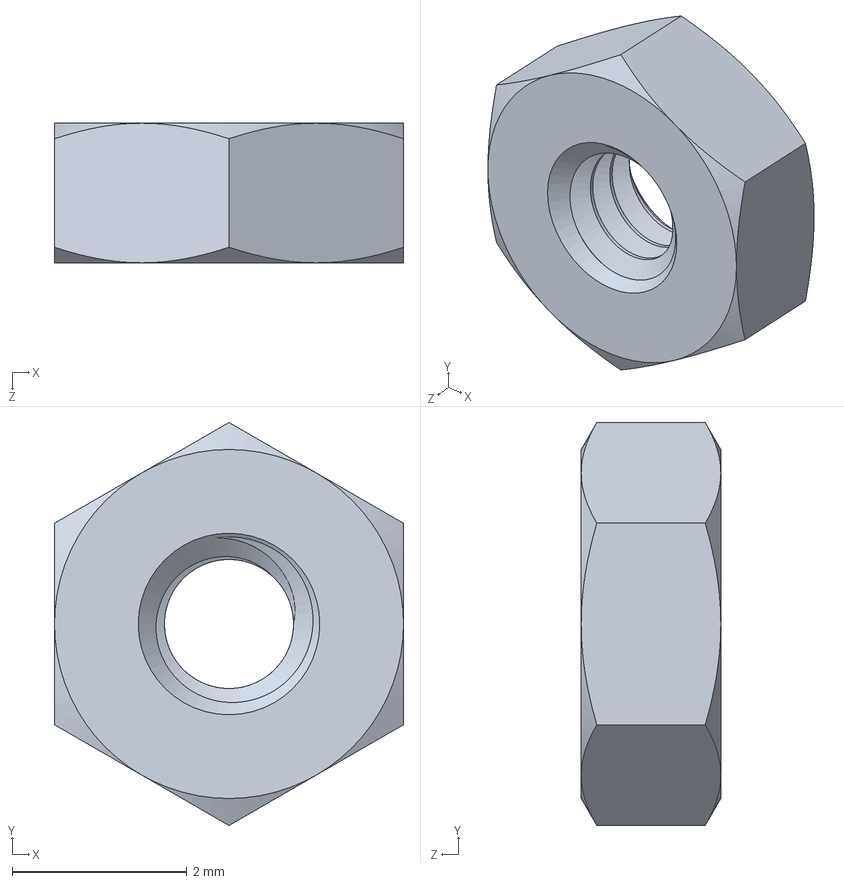
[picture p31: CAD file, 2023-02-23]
mirror_mounts_SW/90690A030_BRASS HEX NUT.SLDPRT
4.00 x 4.62 x 1.60 mm

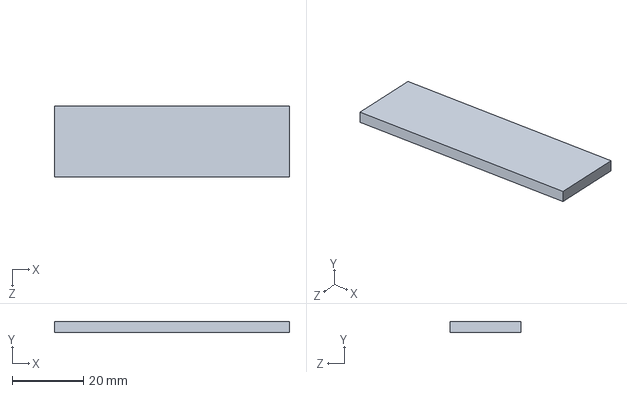
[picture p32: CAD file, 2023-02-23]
mirror_mounts_SW/2312N360_FLAT-SURFACE MACHINE BRACKET.SLDPRT
66.0 x 3.00 x 20.0 mm

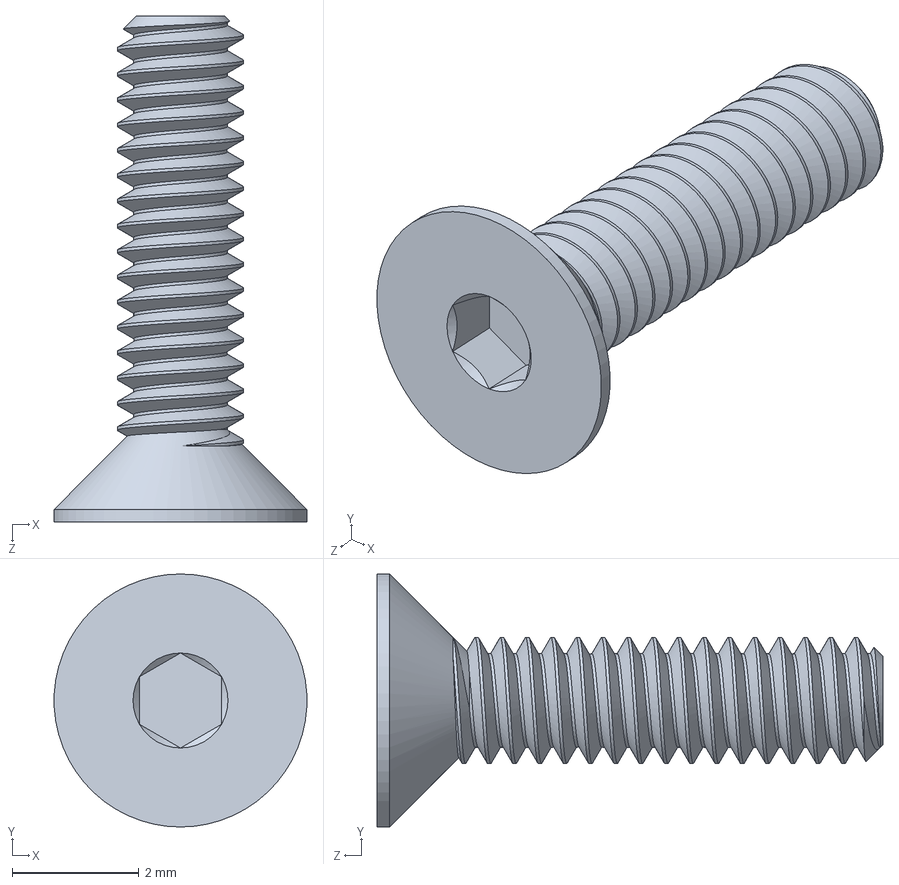
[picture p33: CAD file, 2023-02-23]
mirror_mounts_SW/97595A300_BRASS HEX DRIVE FLAT HEAD SCREW.SLDPRT
3.99 x 4.00 x 8.00 mm

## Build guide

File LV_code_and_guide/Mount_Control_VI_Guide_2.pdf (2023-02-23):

## Contents

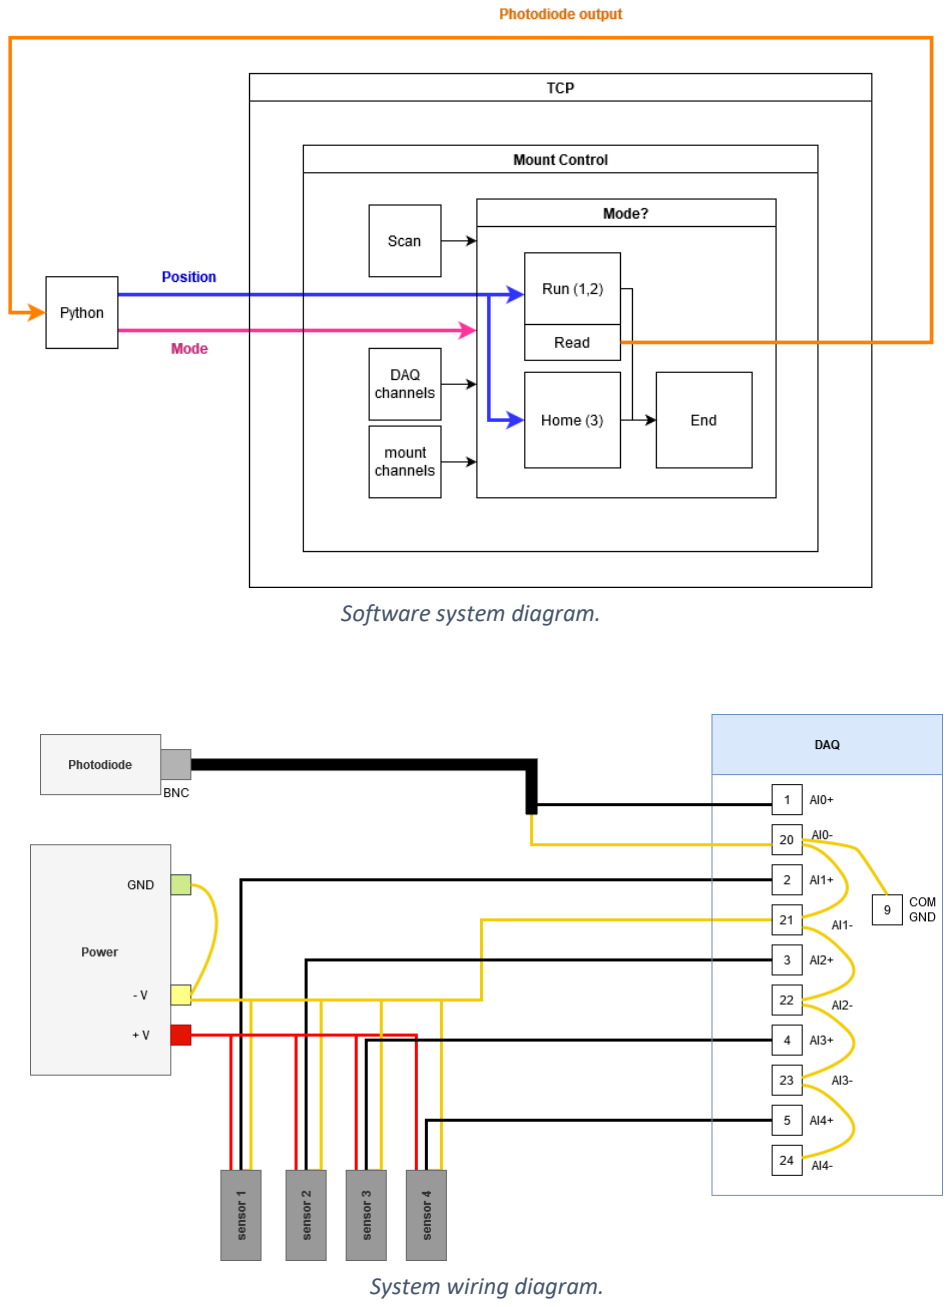
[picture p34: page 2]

Software system diagram.

System wiring diagram.

## Top Level TCP Communication

### TCP Communication

The “TCP_connection” VI is used to send position data from Python file “TCP_bare” to the mount controls subVI. The subVI outputs laser coupling percentage and the value is sent back to Python.

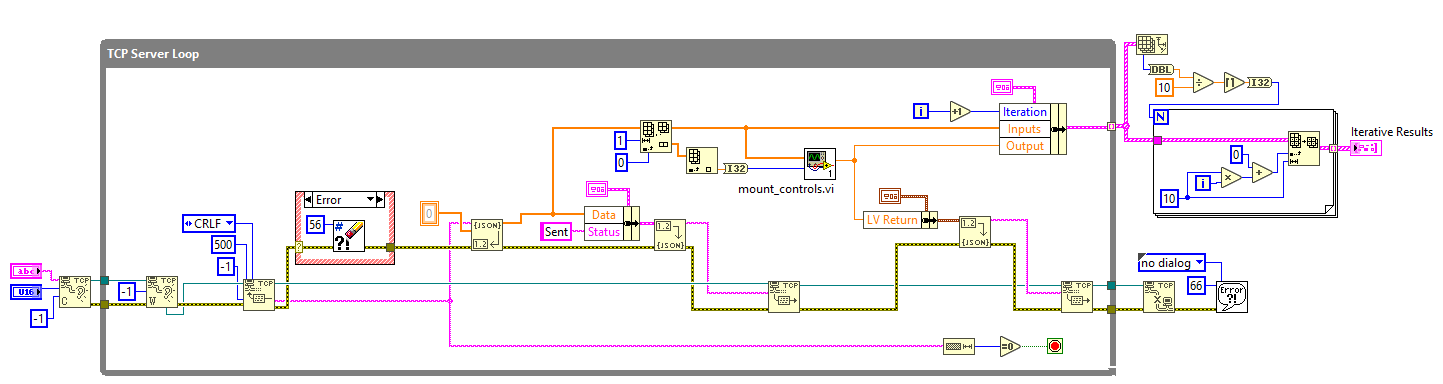
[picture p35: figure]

Full TCP Communication VI.

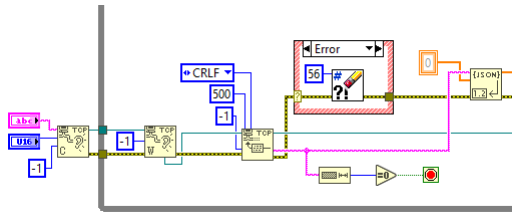
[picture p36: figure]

Read Data from Python
- Initialize by creating TCP listener at the designated port name and #
- Wait on data to be sent from Python
- Read array of position values from Python and unflatten from JSON
- Ignore error 56 (read timeout)
- If sent data string length = 0, stop VI

Send Data to subVI
- Flatten data array and “sent” confirmation and return to Python
- Separate first value of sent array to get “Mode” and the position inputs
- Send mode and positions to “mount_controls” subVI and output percent laser coupling

Initialization and reading Python data.

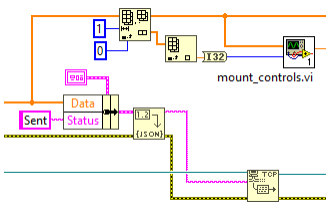
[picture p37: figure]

Send “data received” confirmation to Python and send inputs to mount control subVI.

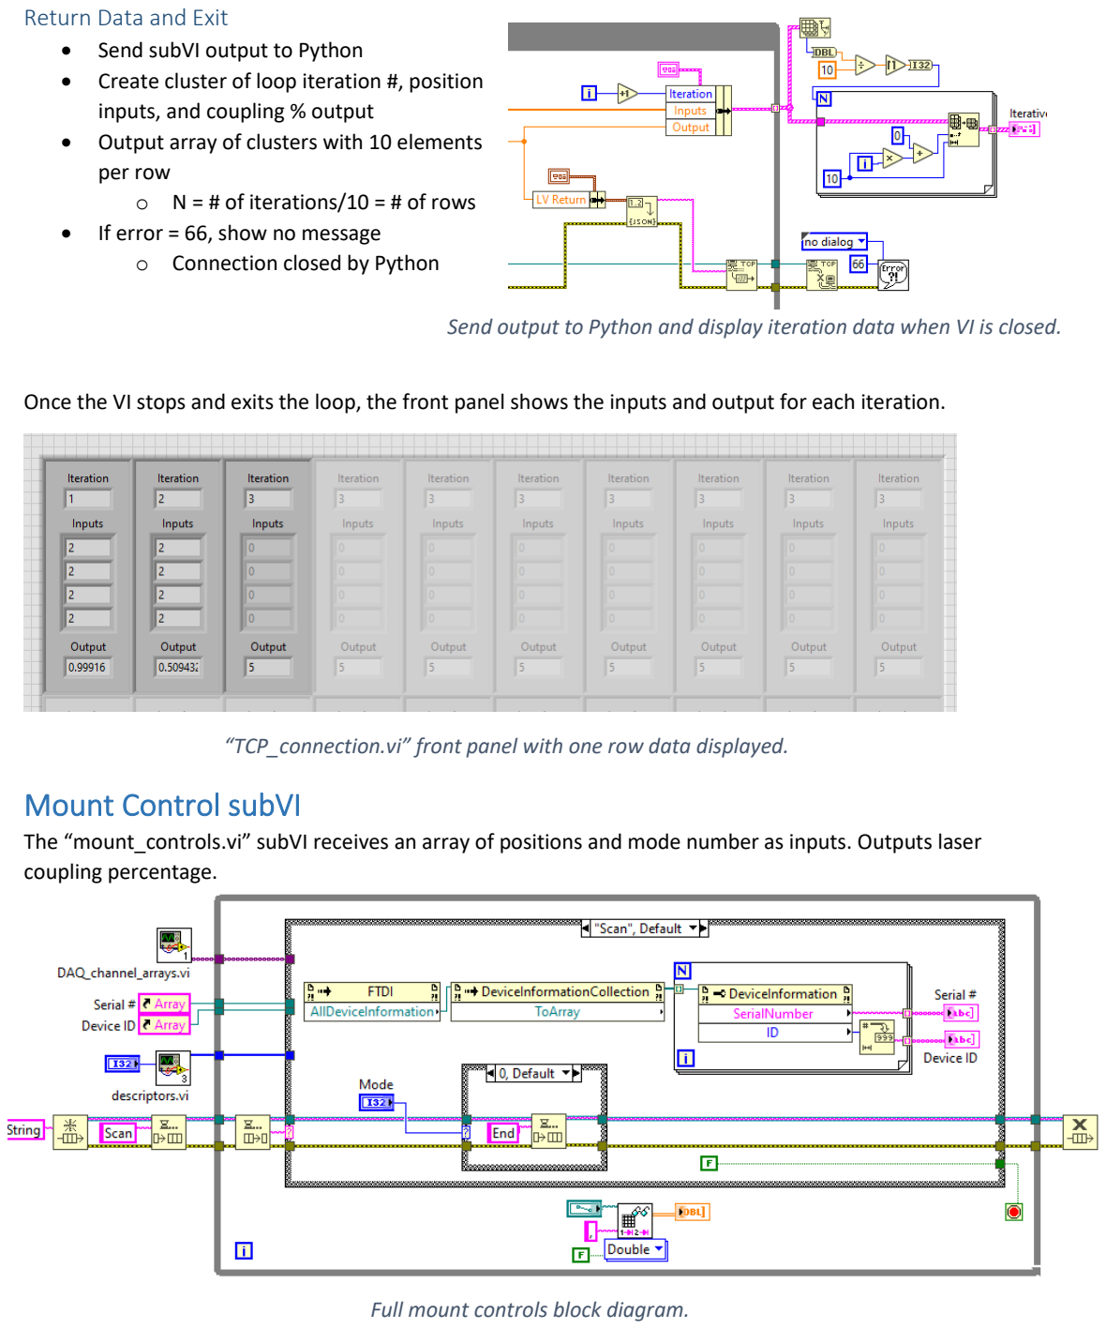
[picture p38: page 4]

Return Data and Exit
- Send subVI output to Python
- Create cluster of loop iteration #, position inputs, and coupling % output
- Output array of clusters with 10 elements per row
- N = # of iterations/10 = # of rows
- If error = 66, show no message
- Connection closed by Python

Once the VI stops and exits the loop, the front panel shows the inputs and output for each iteration.

“TCP_connection.vi” front panel with one row data displayed.

## Mount Control subVI

The “mount_controls.vi” subVI receives an array of positions and mode number as inputs. Outputs laser coupling percentage.

Send output to Python and display iteration data when VI is closed.

Full mount controls block diagram.

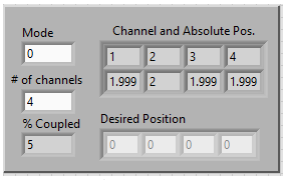
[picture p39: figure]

The front panel displays:

- Mode #, Python input
- Desired position array, Python input
- # of channels, user control input
- Saved position for each channel
- Read from “saved_position.csv”
- Percent of laser coupled, LV output

### Initialization

When the “controls_auto_TCP.vi” VI is run:

- Creates message queue and initializes with “Scan” to get array of serial #’s and device ID’s
- Runs “descriptors.vi” subVI to get array of all controller channels
- Runs “DAQ_channels.vi” subVI to get arrays of DAQ AI channels

DAQ Channels Configuration
The “DAQ_channels” subVI creates an arrays of DAQ analog input channels.

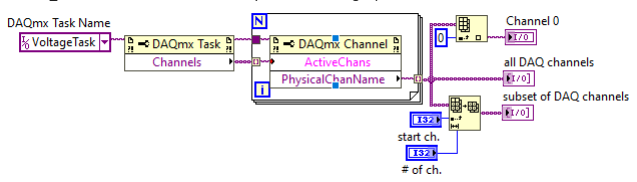
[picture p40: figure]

- Voltage sampling task created in NIMAX referenced for property node to output AI channels
- For loop creates array of the names of DAQ AI channels, N = # of active channels
- Subset of channel array created at user controlled start and length
- Channel 0 separated for reading the photodiode
- 16 analog inputs on the DAQ (AI 0-15), 1-15 can be used to read sensors

Array and queue initialization.

Mount controls front panel display and inputs.

Full block diagram of DAQ channel subVI.

Mount Channels Configuration
The “descriptors.vi” subVI is used to create arrays of channel numbers and labels for the front panel. User inputs “# of channels” on the “mount_controls.vi” front panel.

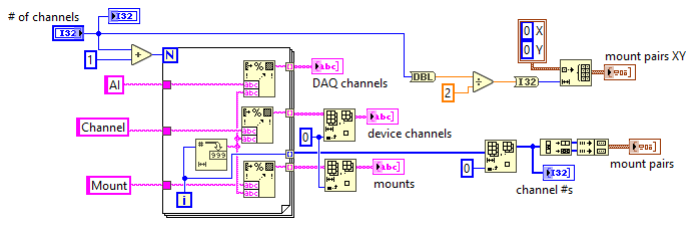
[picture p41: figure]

Descriptors full block diagram. Creates labels for device channels, DAQ channels, and mount clusters.

String Label Arrays
For loop creates array strings to make labels for DAQ channels, device channels, and mounts.
- N = # of channels + 1
- Formats labels and loop “i” into string
- First element (0) deleted from mount and device channel arrays

Channel Numbers and Mount Clusters
Amount of loop iterations is used to create a numeric array of channels and clusters for mount pairs.
- First element (0) deleted from “i” array to get array of channel #’s
- Channel # array is decimated to split into odd and even channels
- Odd and even channels indexed and clustered to get mount channel # pairs
- Cluster of mount channel XY pair controls made size of (# of channels)/2

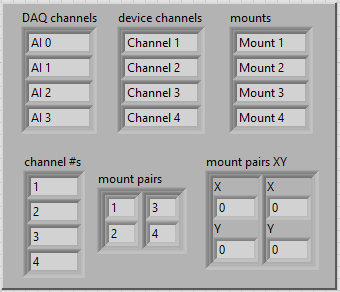
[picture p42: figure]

Descriptors array outputs. String labels (top row) and channel numbers and pair clusters (bottom row).

### Scan Case

Case triggered by initial message in queue when the VI is run.

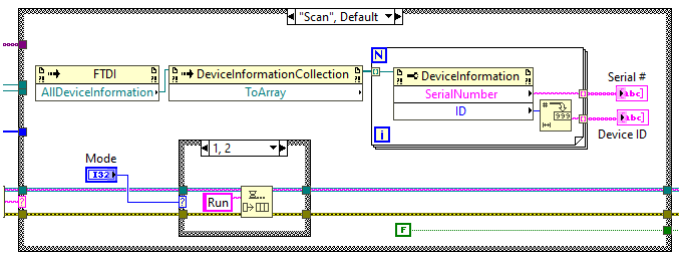
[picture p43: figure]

“Scan” initialization case.

- Collect all info from connected FTDI USB devices (K-cube controllers) and convert to an array
- For loop N = size of device info array; how many controllers are connected
- Property node splits device info into arrays of motor serial numbers and controller IDs
- String arrays are used as a local reference outside of the loop to connect to controllers
- Mode input from TCP connection VI queues message based on user input
- 1 or 2 = “Run”
- 3 = “Home”
- 0/Default = “End”

### Run Case

When a “Run” message is dequeued, channels are moved to the input position and “Read” is queued.

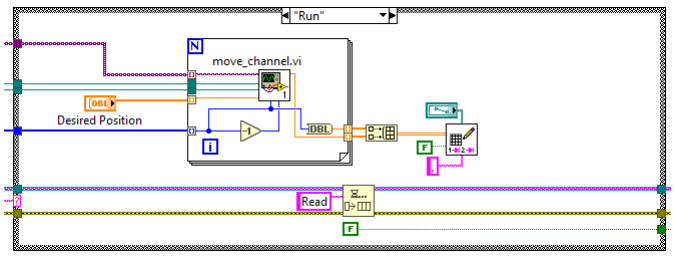
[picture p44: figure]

“Run” case.

- For loop takes inputs of serial #/device ID references and indexes through input arrays of the mount channel, DAQ channel, and desired position
- Runs “move_channel” for all channels and writes absolute position to file when for loop is exited

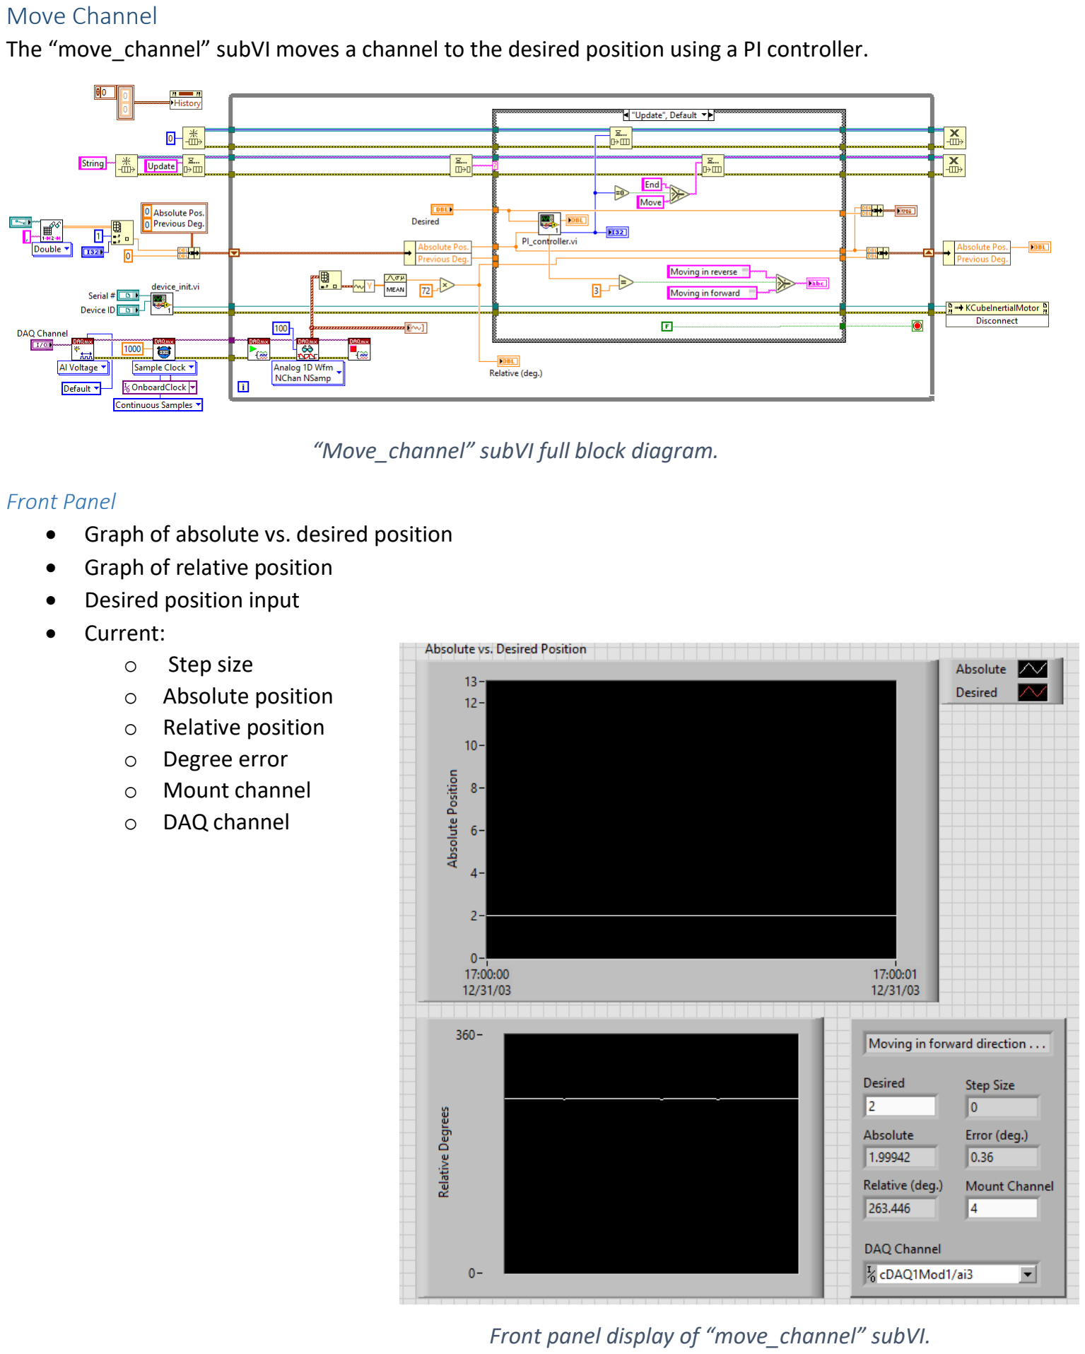
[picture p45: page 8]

Move Channel
The “move_channel” subVI moves a channel to the desired position using a PI controller.

“Move_channel” subVI full block diagram.

Front Panel
- Graph of absolute vs. desired position
- Graph of relative position
- Desired position input
- Current:
- Step size
- Absolute position
- Relative position
- Degree error
- Mount channel
- DAQ channel

Front panel display of “move_channel” subVI.

Initialization
- Absolute vs. Desired Position graph reset
- Step size queue created
- Message queue created and initialized with “Update”
- Saved position file is read
- Position shift register initialized with current channel’s absolute position and 0 for previous degrees
- “device_init” subVI connects to device and controller
- DAQ AI voltage channel is created
- Continuous sampling timer is created with a 1000 Hz (samples per channel/second) sampling rate

Device Initialization

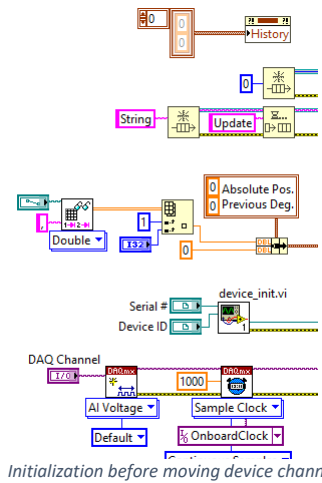
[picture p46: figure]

The “device_init” subVI creates the motor controller and device and connection to the mounts.

To create K-cube motor controllers and motor devices:

- Constructor node creates ref. of
.NET device manager
- Property nodes reads serial # and
device ID string arrays
- Device manager data and string
arrays enter FOR loop
- N = # of controllers

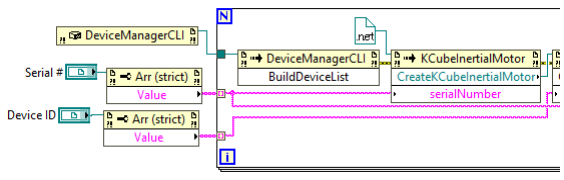
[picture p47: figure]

- Device manager property builds list of
devices from constructor node
- Property node creates motor device using the serial #, refnum in = motor class constant

Create K-cube motor controllers and motor devices.

“device_init” full subVI.

Initialization before moving device channel.

“CreateKCubeInertialMotor” used as reference to connect to:

- K-cube controller with device ID
- Inertial motor with serial #
- Get motor configuration to initialize default settings

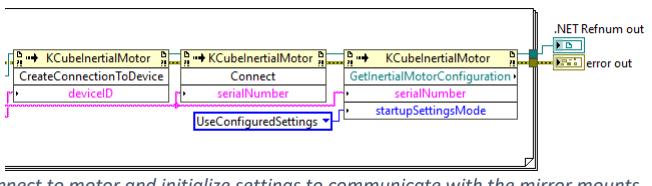
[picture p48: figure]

Sensor Sampling
Each time the loop runs, the sensor connected to the current DAQ channel is sampled.
- Start DAQ task
- Read AI with 100 samp/ch
- Stop DAQ task
- Get voltage data from waveform output and average the samples
- Multiply by 72 (360/5) and output relative deg.
- Plots waveform graph of relative degrees

Update Case

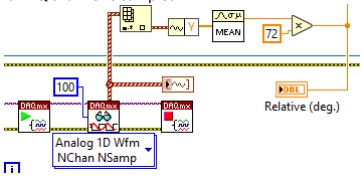
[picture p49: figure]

When an “Update” message is dequeued, the PI controller determines the step size needed. A “Move” or “End” messaged is queued based on whether the step size output = 0.

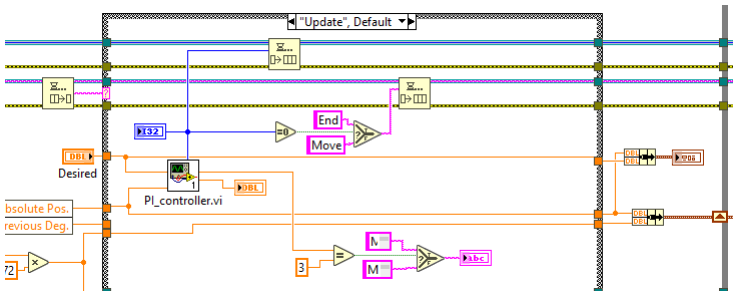
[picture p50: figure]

“Update” case while moving channels to get step size.

- Writes current relative position to “previous degrees” shift register
- Desired position and absolute position compared by the PI controller
- Outputs and enqueues step size
- Checks if step size = 0 and if true, queue “End” message; if false, queue “Move”
- Checks direction and outputs indicator message on front panel

Connect to motor and initialize settings to communicate with the mirror mounts.

Sensor sampling and conversion to relative degrees.

PI Controller

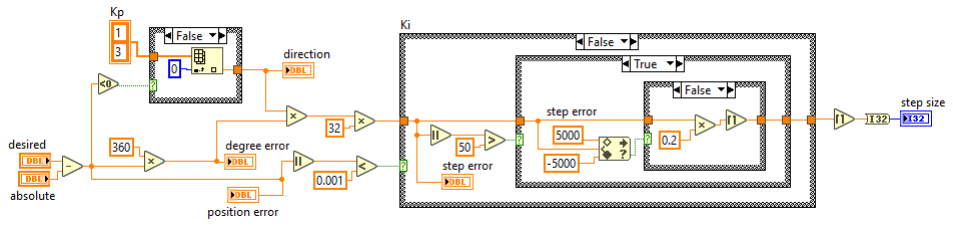
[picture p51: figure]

PI Controller subVI full block diagram.

- Position error = desired – absolute
- First case structure “Kp” checks if position error < 0 to get direction
- True = reverse = 3, false = forward = 1
- Position error multiplied by 360 to get degree error
- Degree error x direction x 32 = approximate step error
- Forward approximately 32 steps/degree forward and 3 times faster than reverse
- Second case structure “Ki” checks if absolute position error < 0.001
- If true, step size = 0
- If false, checks if step error is > 50
- If false, step size = step error / 2
- If true, check if within +/- 5000 step range
- If within range, step size = step error
- If out of range, step size = step error / 5

Move Case
When a “Move” message is dequeued, the channel is moved by n steps and queues “Check” message.

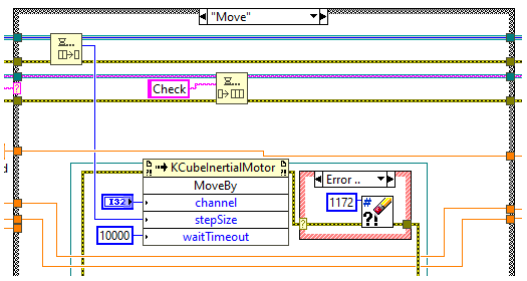
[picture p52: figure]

Move channel by PI controller designated step size.

- Step size dequeued and current channel moved by input step size
- If error = 1172, ignore
- 1172 = timeout; has not received a second message
- Enqueue “Check” message to get absolute position

Check Case
When a “Check” message is dequeued, absolute position stored in the shift register and relative position before and after “Move” case is used to update absolute position. “Update” message in enqueued.

“Check” case to calculate change in absolute position and update shift register.

- Absolute position x 360 to get absolute degrees
- Change in degrees after moving = relative deg. – previous deg.
- Check if desired – absolute position < 0 to get direction
- T: Reverse = CW = + V/degrees = - steps (towards mirror)
- F: Forward = CCW = - V/degrees = + steps (away from mirror)
- If direction = reverse, check if change in deg. > 0:
- T: absolute pos. = absolute deg. – change in deg.
- F: absolute pos. = absolute deg. – (relative deg. + (360 – previous deg.))
- If direction = forward, check if change in deg. < 0:
- T: absolute pos. = absolute deg. + │change in deg.│
- F: absolute pos. = absolute deg. + (previous deg. + (360 – relative deg.))

End Case and Termination
When an “End” message is dequeued, the loop is stopped and references are closed.
- Loop stop condition = T, loop is exited
- Message and step queues are released
and motor is disconnected
- Outputs absolute position

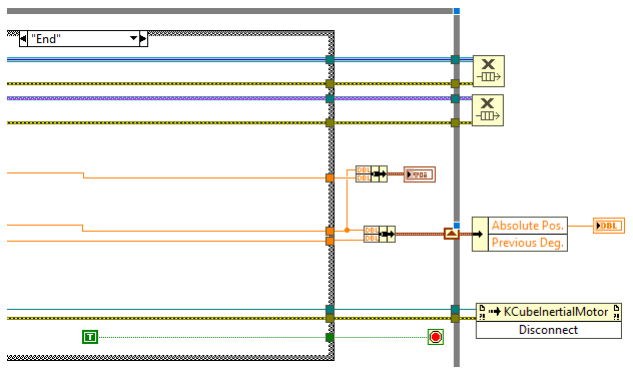
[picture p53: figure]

Moving VI “End” case and subVI termination.

### Read Case

When a “Read” message is dequeued, the photodiode is sampled and laser coupling % is output.

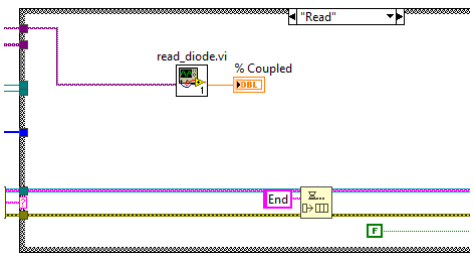
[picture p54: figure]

“Read” case in mount control VI.

Full block diagram for “read_diode” subVI.

- Channel 0 of the DAQ is created and read continuously
- 100 samples from the power meter are multipled by 100 and averaged
- Power meter response (photodiode stand-in) = 1 V/mV
- % coupled output

### Home Case

When a “Home” message is dequeued, the channels are homed and their saved position is set to 0.

- For loop takes inputs of serial #/device ID references
- Indexes through input arrays of the mount channel
and DAQ channels
- Runs “home_channel” for all channels
- Writes 0 to position file when for loop is exited

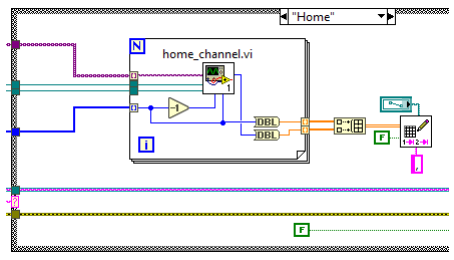
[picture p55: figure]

Mount Control VI “Home” case.

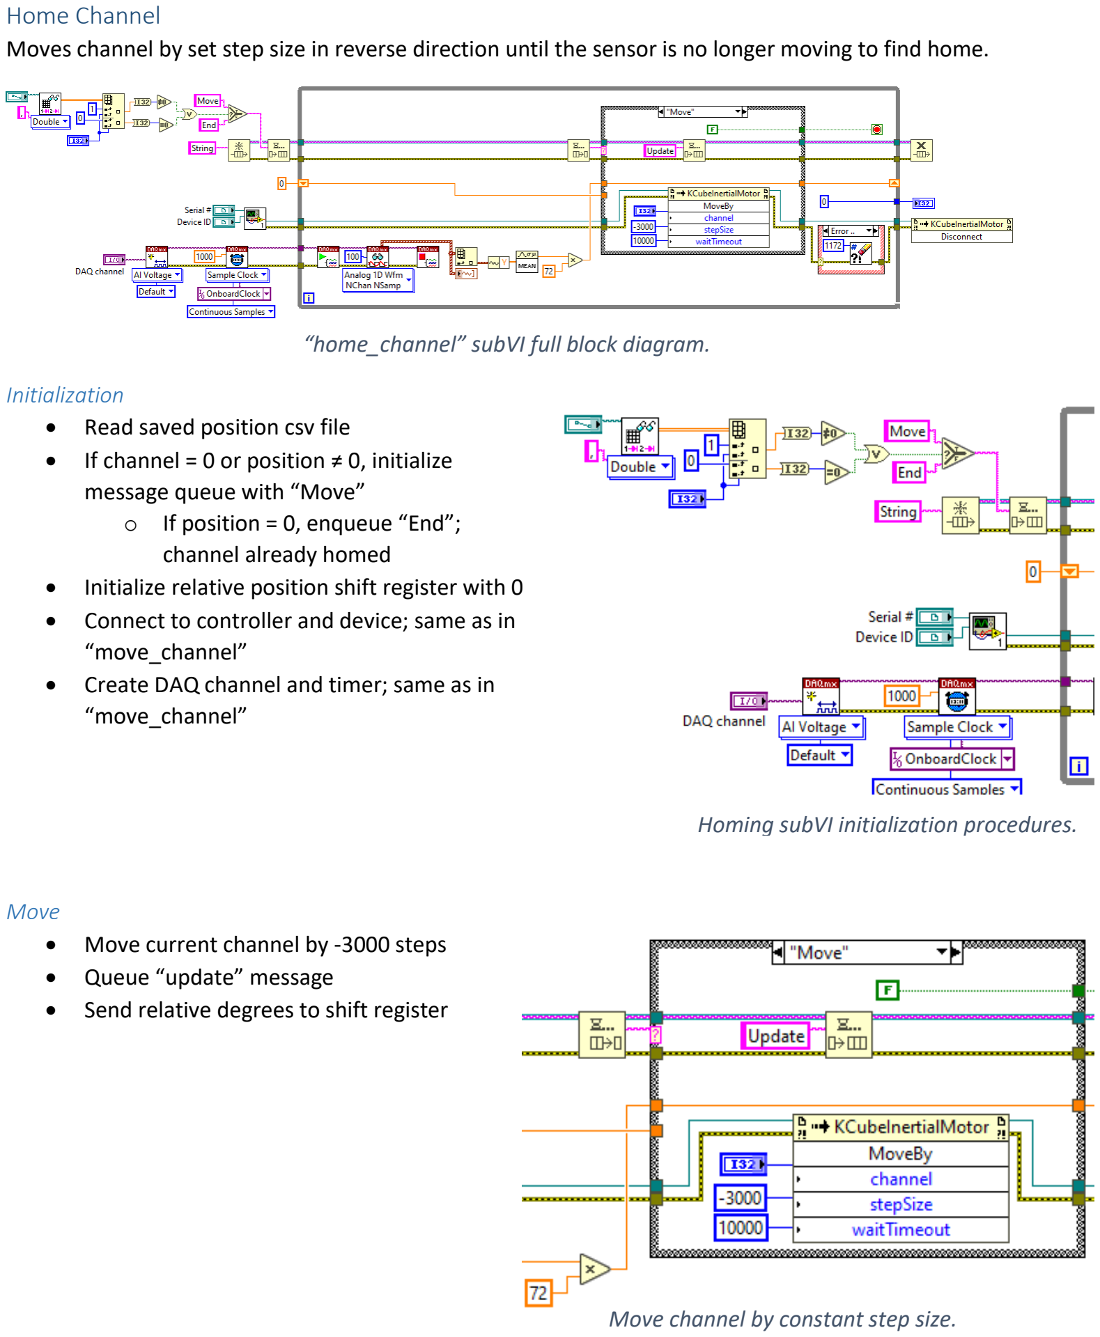
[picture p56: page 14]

Home Channel
Moves channel by set step size in reverse direction until the sensor is no longer moving to find home.

Initialization
- Read saved position csv file
- If channel = 0 or position ≠ 0, initialize message queue with “Move”
- If position = 0, enqueue “End”; channel already homed
- Initialize relative position shift register with 0
- Connect to controller and device; same as in “move_channel”
- Create DAQ channel and timer; same as in “move_channel”

Move
- Move current channel by -3000 steps
- Queue “update” message
- Send relative degrees to shift register

“home_channel” subVI full block diagram.

Homing subVI initialization procedures.

Move channel by constant step size.

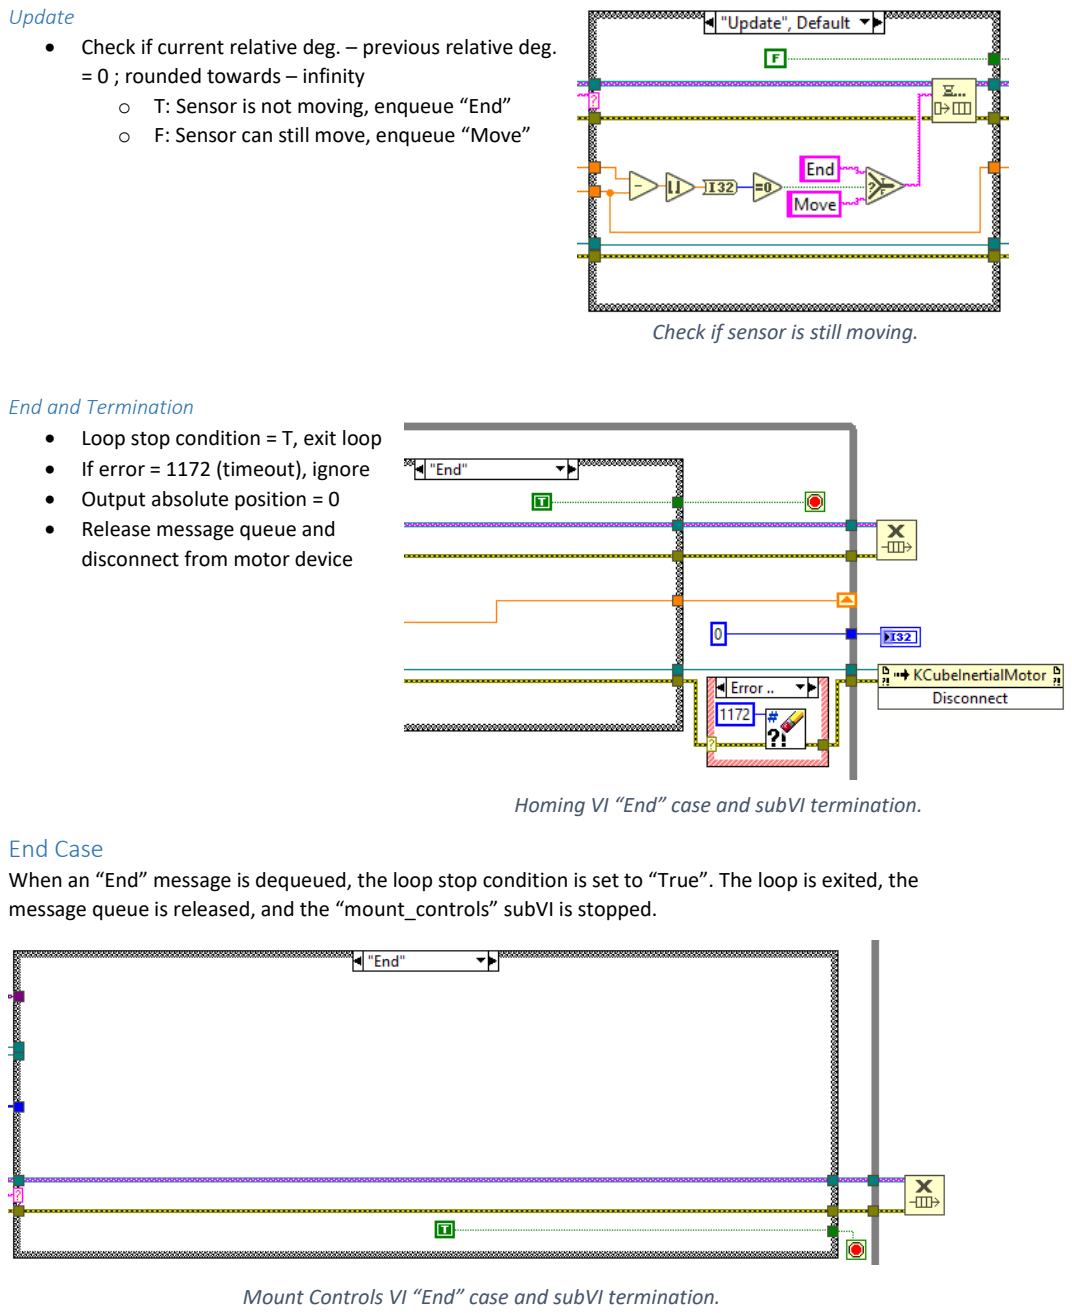
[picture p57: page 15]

Update
- Check if current relative deg. – previous relative deg. = 0 ; rounded towards – infinity
- T: Sensor is not moving, enqueue “End”
- F: Sensor can still move, enqueue “Move”

End and Termination
- Loop stop condition = T, exit loop
- If error = 1172 (timeout), ignore
- Output absolute position = 0
- Release message queue and disconnect from motor device

### End Case

When an “End” message is dequeued, the loop stop condition is set to “True”. The loop is exited, the message queue is released, and the “mount_controls” subVI is stopped.

Mount Controls VI “End” case and subVI termination.

Homing VI “End” case and subVI termination.

Check if sensor is still moving.

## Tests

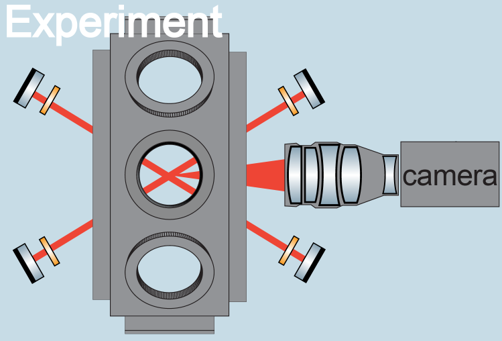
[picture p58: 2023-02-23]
readme_graphics/experiment_s1.png
